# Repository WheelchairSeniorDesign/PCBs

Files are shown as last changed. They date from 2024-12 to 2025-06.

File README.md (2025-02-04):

# PCB Design in Git

- We will be using git to store KiCad files as well so that we can have a running record of them.
- Put all the PCBs in a subfolder in the PCB repo.
- Make a branch for your board, and only work on that board on the corresponding branch.
- Don’t delete your branch once you merge it; keep making changes on that branch.
- Only one person should work on a board at a time, and all changes should be committed before the next person works on it.

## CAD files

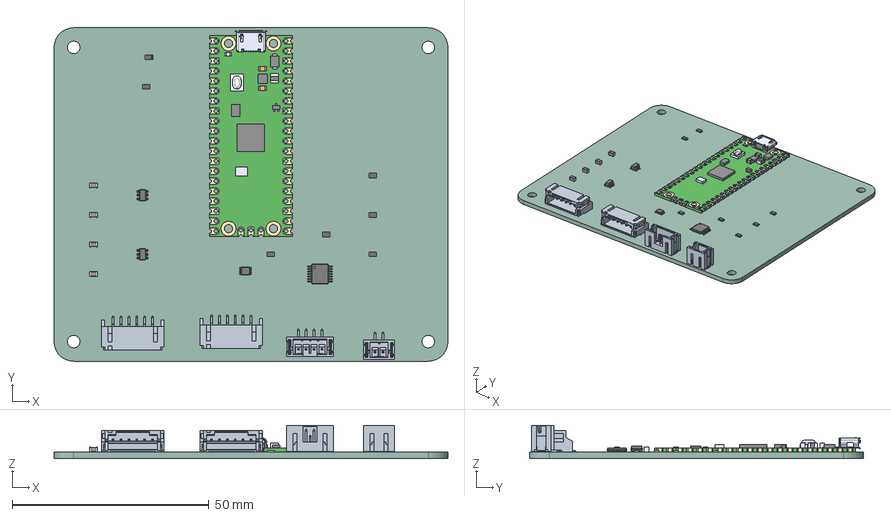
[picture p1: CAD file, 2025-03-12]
MotorSignalConversion/MotorSignalConversion.step
100.0 x 84.7 x 8.40 mm
R_0805_2012Metric x 7
SxBwhite6 x 2
C_0805_2012Metric x 4
B2B-PH-SM4-TB
VSSOP_8_23x2mm_P05mm
SOT_23_6 x 2
TSSOP_14_44x5mm_P065mm
SC0915
B4B-PH-SM4-TB
MotorSignalConversion_PCB

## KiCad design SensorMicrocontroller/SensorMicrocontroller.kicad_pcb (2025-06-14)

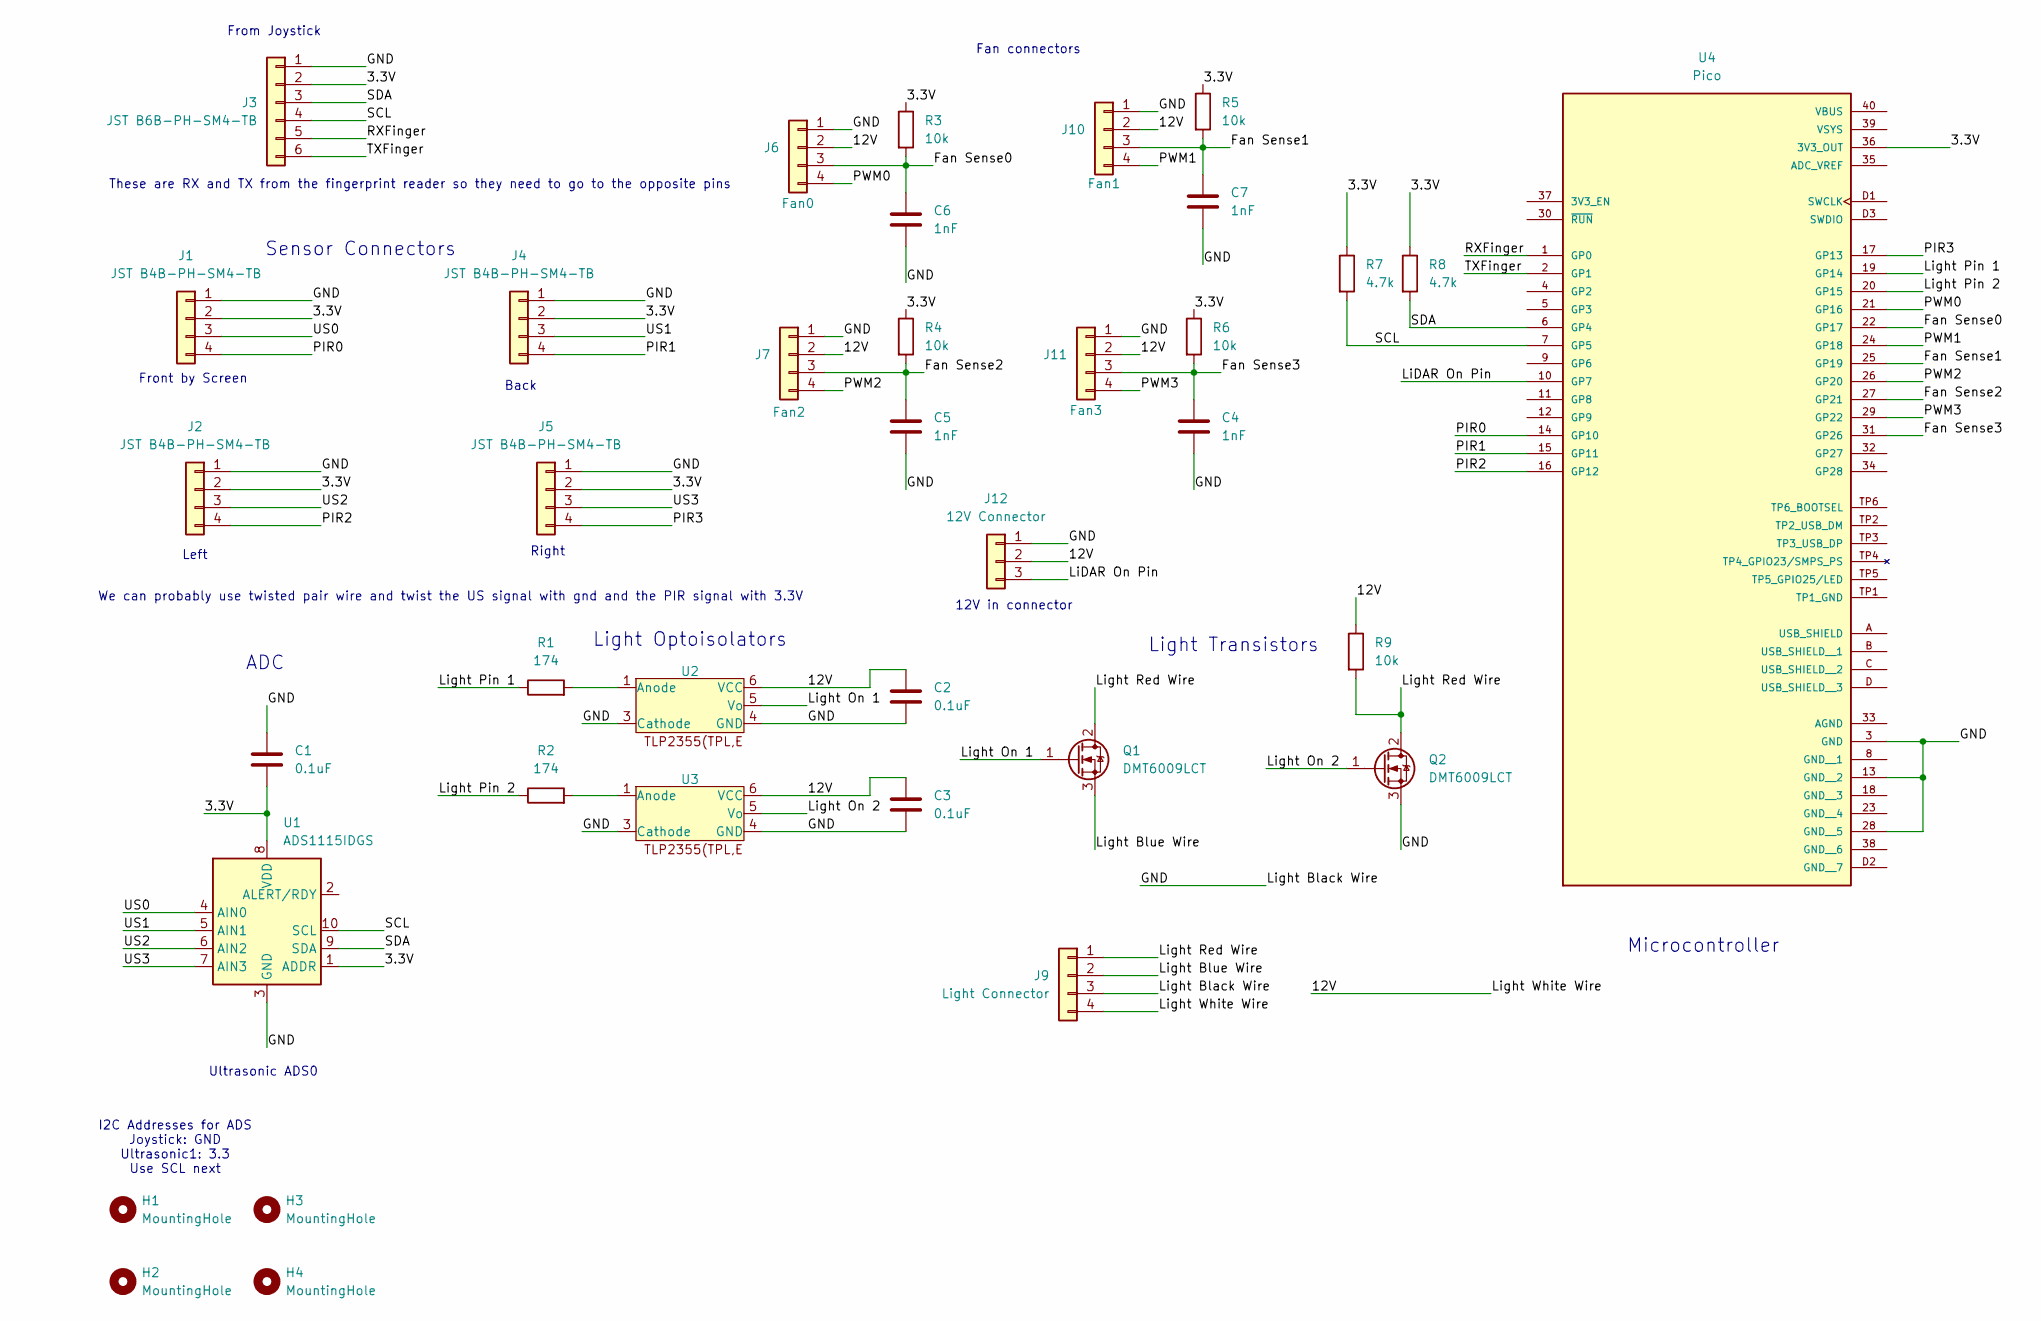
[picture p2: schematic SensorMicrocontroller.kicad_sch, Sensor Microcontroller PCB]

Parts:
C1, C2, C3: 0.1uF; C_0805_2012Metric; Manufacturer Part Number CC0805KRX7R9BB104
C4, C5, C6, C7: 1nF; C_0805_2012Metric; Manufacturer Part Number C0805C102K4RACTU
H1, H2, H3, H4: MountingHole; MountingHole_3.2mm_M3_ISO7380_Pad
J1, J2, J4, J5: JST B4B-PH-SM4-TB; JST_PH_B4B-PH-SM4-TB_1x04-1MP_P2.00mm_Vertical; Manufacturer Part Number B4B-PH-SM4-TB
J3: JST B6B-PH-SM4-TB; JST_PH_B6B-PH-SM4-TB_1x06-1MP_P2.00mm_Vertical; Manufacturer Part Number B6B-PH-SM4-TB
J6, J7, J10, J11: FanPinHeader_1x04_P2.54mm_Vertical; Manufacturer Part Number 0470531000
J9: Light Connector; JST_EH_B4B-EH-A_1x04_P2.50mm_Vertical; Manufacturer Part Number B4B-EH-A
J12: 12V Connector; JST_PH_B3B-PH-SM4-TB_1x03-1MP_P2.00mm_Vertical; Manufacturer Part Number B3B-PH-SM4-TB
Q1, Q2: DMT6009LCT; TO-220-3_Vertical; Manufacturer Part Number DMT6009LCT
R1, R2: 174; R_0805_2012Metric; Manufacturer Part Number RC0805FR-07174RL
R3, R4, R5, R6, R9: 10k; R_0805_2012Metric; Manufacturer Part Number RR1220P-103-D
R7, R8: 4.7k; R_0805_2012Metric; Manufacturer Part Number CRCW08054K70FKEAC
U1: ADS1115IDGS; VSSOP-10_3x3mm_P0.5mm; Manufacturer Part Number ADS1115IDGSR
U2, U3: Optoisolators; SO-5-6_4.55x3.7mm_P1.27mm; Manufacturer Part Number TLP2355(TPL,E
U4: Pico; pico; PARTREV 1.9

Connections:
/3.3V: C1.2, J1.2, J2.2, J3.2, J4.2, J5.2, R3.1, R4.1, R5.1, R6.1, R7.1, R8.1, U1.1 (ADDR), U1.8 (VDD), U4.36 (3V3_OUT)
/12V: C2.1, C3.1, J6.2, J7.2, J9.4, J10.2, J11.2, J12.2, R9.1, U2.6 (VCC), U3.6 (VCC)
/Fan Sense0: C6.1, J6.3, R3.2, U4.22 (GP17)
/Fan Sense1: C7.1, J10.3, R5.2, U4.25 (GP19)
/Fan Sense2: C5.1, J7.3, R4.2, U4.27 (GP21)
/Fan Sense3: C4.1, J11.3, R6.2, U4.31 (GP26)
/GND: C1.1, C2.2, C3.2, C4.2, C5.2, C6.2, C7.2, J1.1, J2.1, J3.1, J4.1, J5.1, J6.1, J7.1, J9.3, J10.1, J11.1, J12.1, Q2.3 (S), U1.3 (GND), U2.3 (Cathode), U2.4 (GND), U3.3 (Cathode), U3.4 (GND), U4.3 (GND), U4.13 (GND__2), U4.28 (GND__5)
/LiDAR On Pin: J12.3, U4.10 (GP7)
/Light Blue Wire: J9.2, Q1.3 (S)
/Light On 1: Q1.1 (G), U2.5 (Vo)
/Light On 2: Q2.1 (G), U3.5 (Vo)
/Light Pin 1: R1.1, U4.19 (GP14)
/Light Pin 2: R2.1, U4.20 (GP15)
/Light Red Wire: J9.1, Q1.2 (D), Q2.2 (D), R9.2
/PIR0: J1.4, U4.14 (GP10)
/PIR1: J4.4, U4.15 (GP11)
/PIR2: J2.4, U4.16 (GP12)
/PIR3: J5.4, U4.17 (GP13)
/PWM0: J6.4, U4.21 (GP16)
/PWM1: J10.4, U4.24 (GP18)
/PWM2: J7.4, U4.26 (GP20)
/PWM3: J11.4, U4.29 (GP22)
/RXFinger: J3.5, U4.1 (GP0)
/SCL: J3.4, R7.2, U1.10 (SCL), U4.7 (GP5)
/SDA: J3.3, R8.2, U1.9 (SDA), U4.6 (GP4)
/TXFinger: J3.6, U4.2 (GP1)
/US0: J1.3, U1.4 (AIN0)
/US1: J4.3, U1.5 (AIN1)
/US2: J2.3, U1.6 (AIN2)
/US3: J5.3, U1.7 (AIN3)
unnamed: R1.2, U2.1 (Anode)
unnamed: R2.2, U3.1 (Anode)

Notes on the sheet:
Microcontroller
Right
ADC
Light Transistors
Back
Sensor Connectors
Left
These are RX and TX from the fingerprint reader so they need to go to the opposite pins
From Joystick
Front by Screen
Fan connectors
Light Optoisolators
Ultrasonic ADS0
I2C Addresses for ADS Joystick: GND Ultrasonic1: 3.3 Use SCL next
12V in connector
We can probably use twisted pair wire and twist the US signal with gnd and the PIR signal with 3.3V

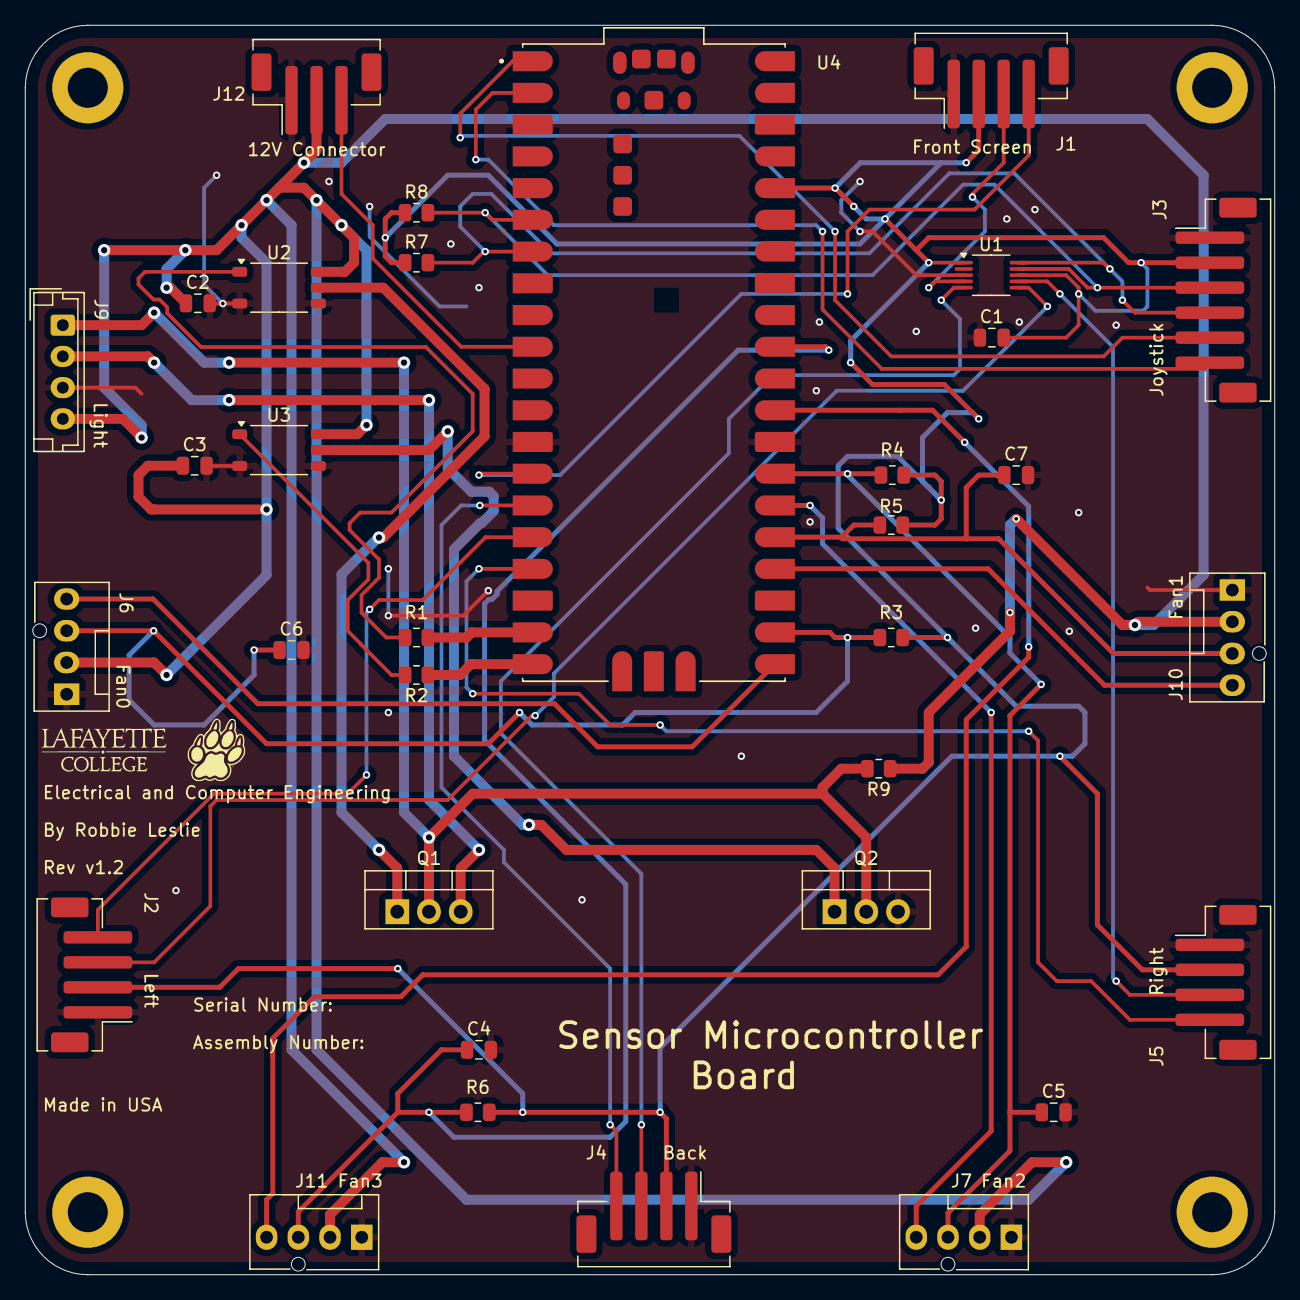
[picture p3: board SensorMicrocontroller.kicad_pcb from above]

Board: 2 copper layers, 100.0 x 100.0 mm, 37 parts (0 on the bottom side), 32 nets.

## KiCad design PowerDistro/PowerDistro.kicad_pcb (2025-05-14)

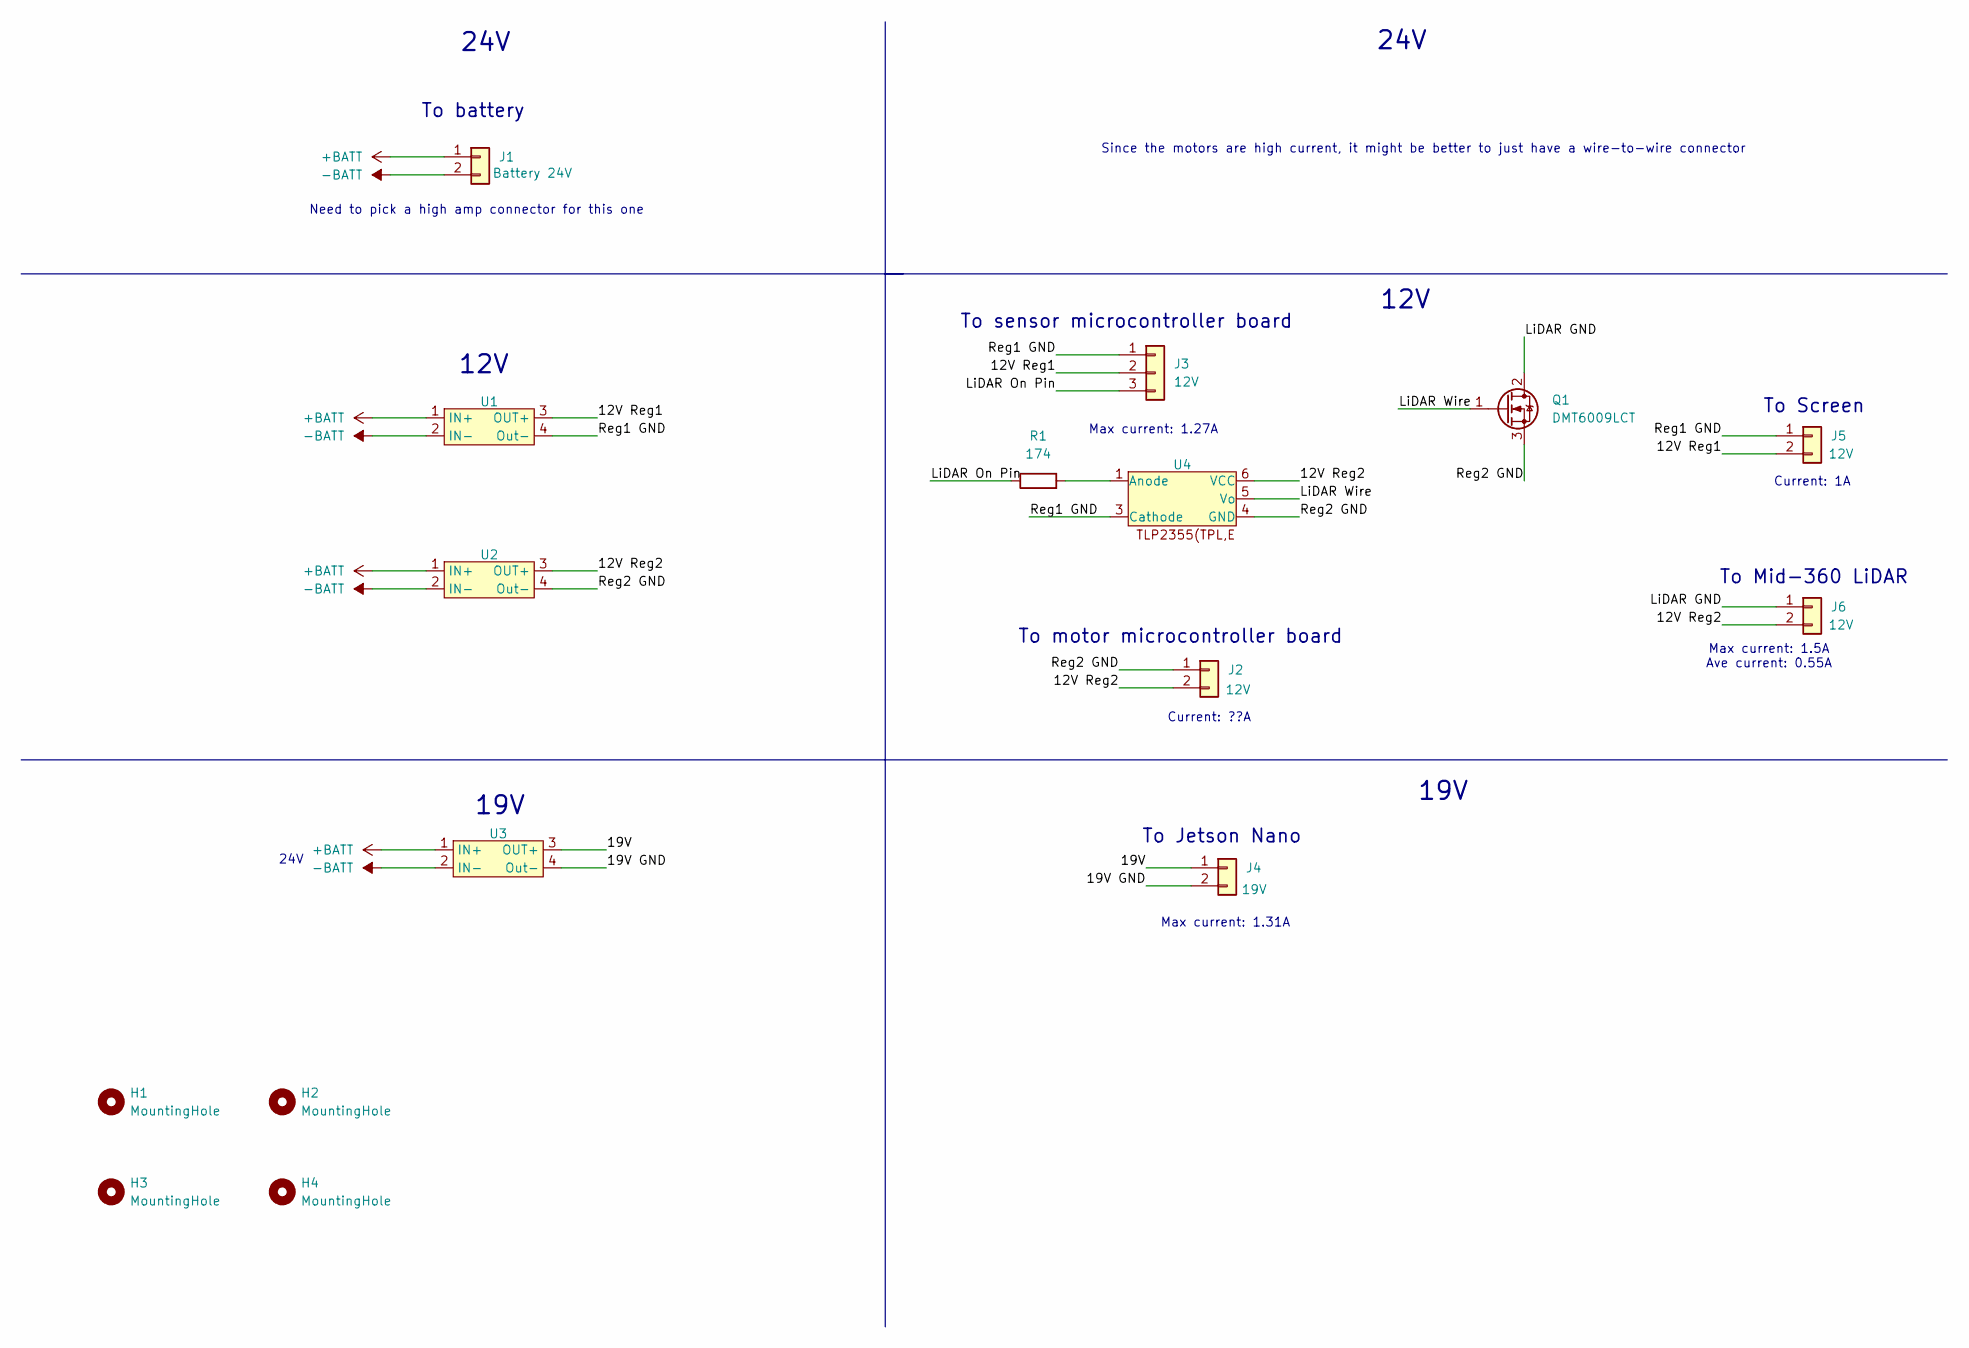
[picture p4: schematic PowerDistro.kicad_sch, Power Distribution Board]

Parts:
H1, H2, H3, H4: MountingHole; MountingHole_3.2mm_M3_ISO7380_Pad
J1: Molex_Mini-Fit_Jr_5566-02A_2x01_P4.20mm_Vertical; Manufacturer Part Number 0039290023
J2: JST_PH_S2B-PH-SM4-TB_1x02-1MP_P2.00mm_Horizontal; Manufacturer Part Number S2B-PH-SM4-TB
J3: 12V; JST_PH_S3B-PH-SM4-TB_1x03-1MP_P2.00mm_Horizontal; Manufacturer Part Number S3B-PH-SM4-TB
J4, J5, J6: JST_XH_S2B-XH-A-1_1x02_P2.50mm_Horizontal; Manufacturer Part Number S2B-XH-A-1
Q1: DMT6009LCT; TO-220-3_Vertical; Manufacturer Part Number DMT6009LCT
R1: 174; R_0805_2012Metric; Manufacturer Part Number RC0805FR-07174RL
U1, U2, U3: LM2596
U4: Optoisolators; SO-5-6_4.55x3.7mm_P1.27mm; Manufacturer Part Number TLP2355(TPL,E

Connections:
+BATT: J1.1, U1.1 (IN+), U2.1 (IN+), U3.1 (IN+)
-BATT: J1.2, U1.2 (IN-), U2.2 (IN-), U3.2 (IN-)
/12V Reg1: J3.2, J5.2, U1.3 (OUT+)
/12V Reg2: J2.2, J6.2, U2.3 (OUT+), U4.6 (VCC)
/19V: J4.1, U3.3 (OUT+)
/19V GND: J4.2, U3.4 (Out-)
/LiDAR GND: J6.1, Q1.2 (D)
/LiDAR On Pin: J3.3, R1.1
/LiDAR Wire: Q1.1 (G), U4.5 (Vo)
/Reg1 GND: J3.1, J5.1, U1.4 (Out-), U4.3 (Cathode)
/Reg2 GND: J2.1, Q1.3 (S), U2.4 (Out-), U4.4 (GND)
unnamed: R1.2, U4.1 (Anode)

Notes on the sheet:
Current: 1A
24V
To Jetson Nano
To battery
19V
12V
Max current: 1.27A
Since the motors are high current, it might be better to just have a wire-to-wire connector
To sensor microcontroller board
To motor microcontroller board
To Mid-360 LiDAR
Need to pick a high amp connector for this one
To Screen
Current: ??A
Max current: 1.5A Ave current: 0.55A
Max current: 1.31A

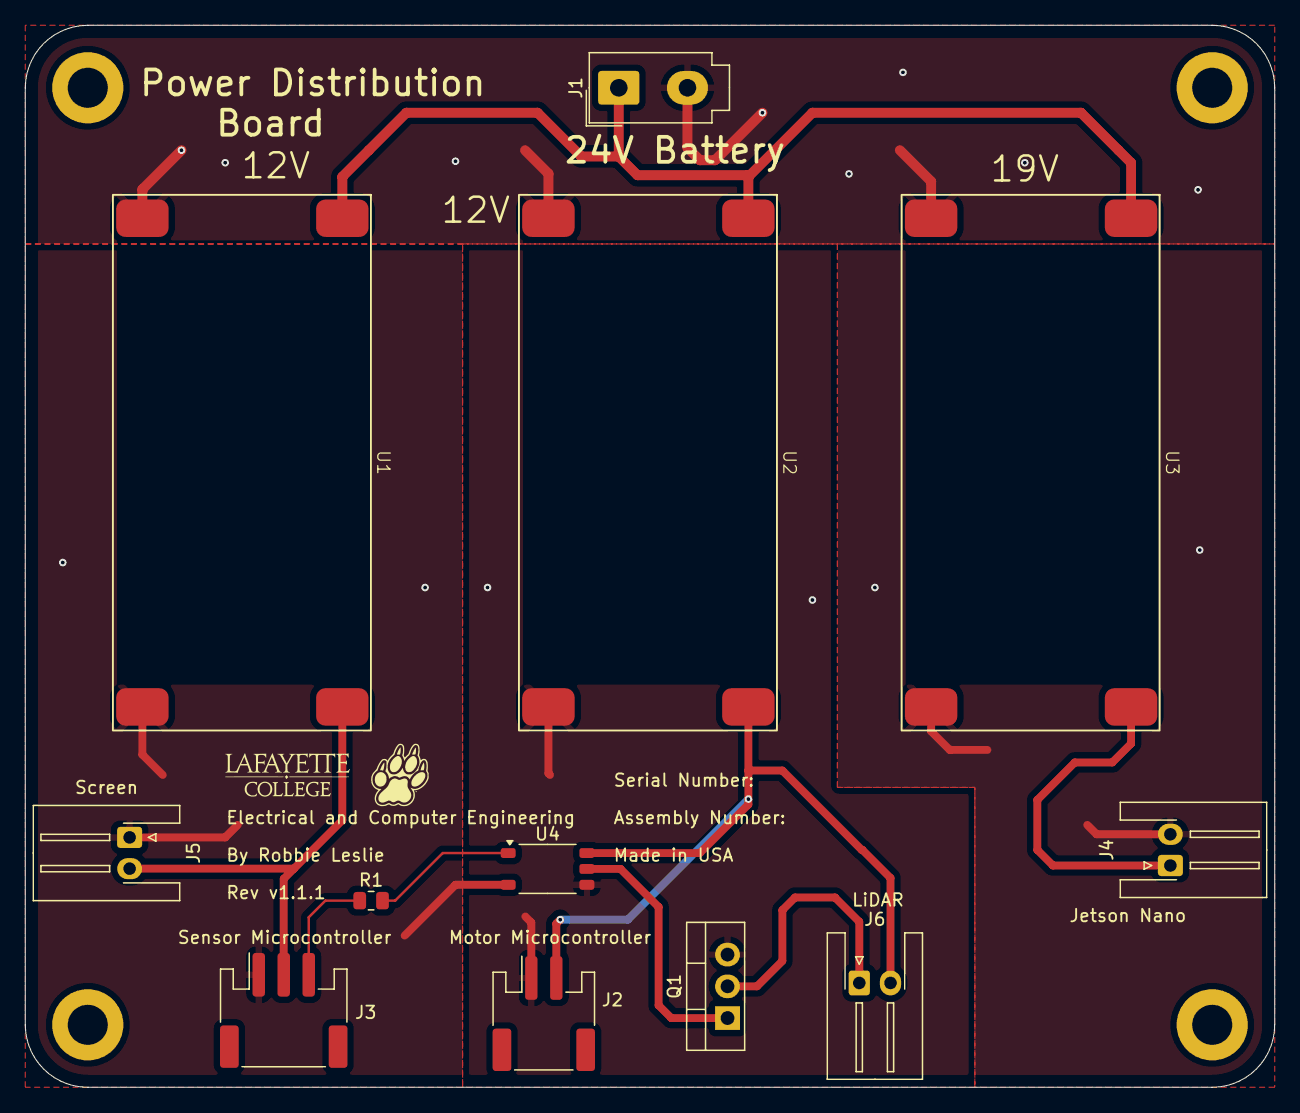
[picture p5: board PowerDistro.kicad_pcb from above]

Board: 2 copper layers, 100.0 x 85.0 mm, 16 parts (0 on the bottom side), 12 nets.

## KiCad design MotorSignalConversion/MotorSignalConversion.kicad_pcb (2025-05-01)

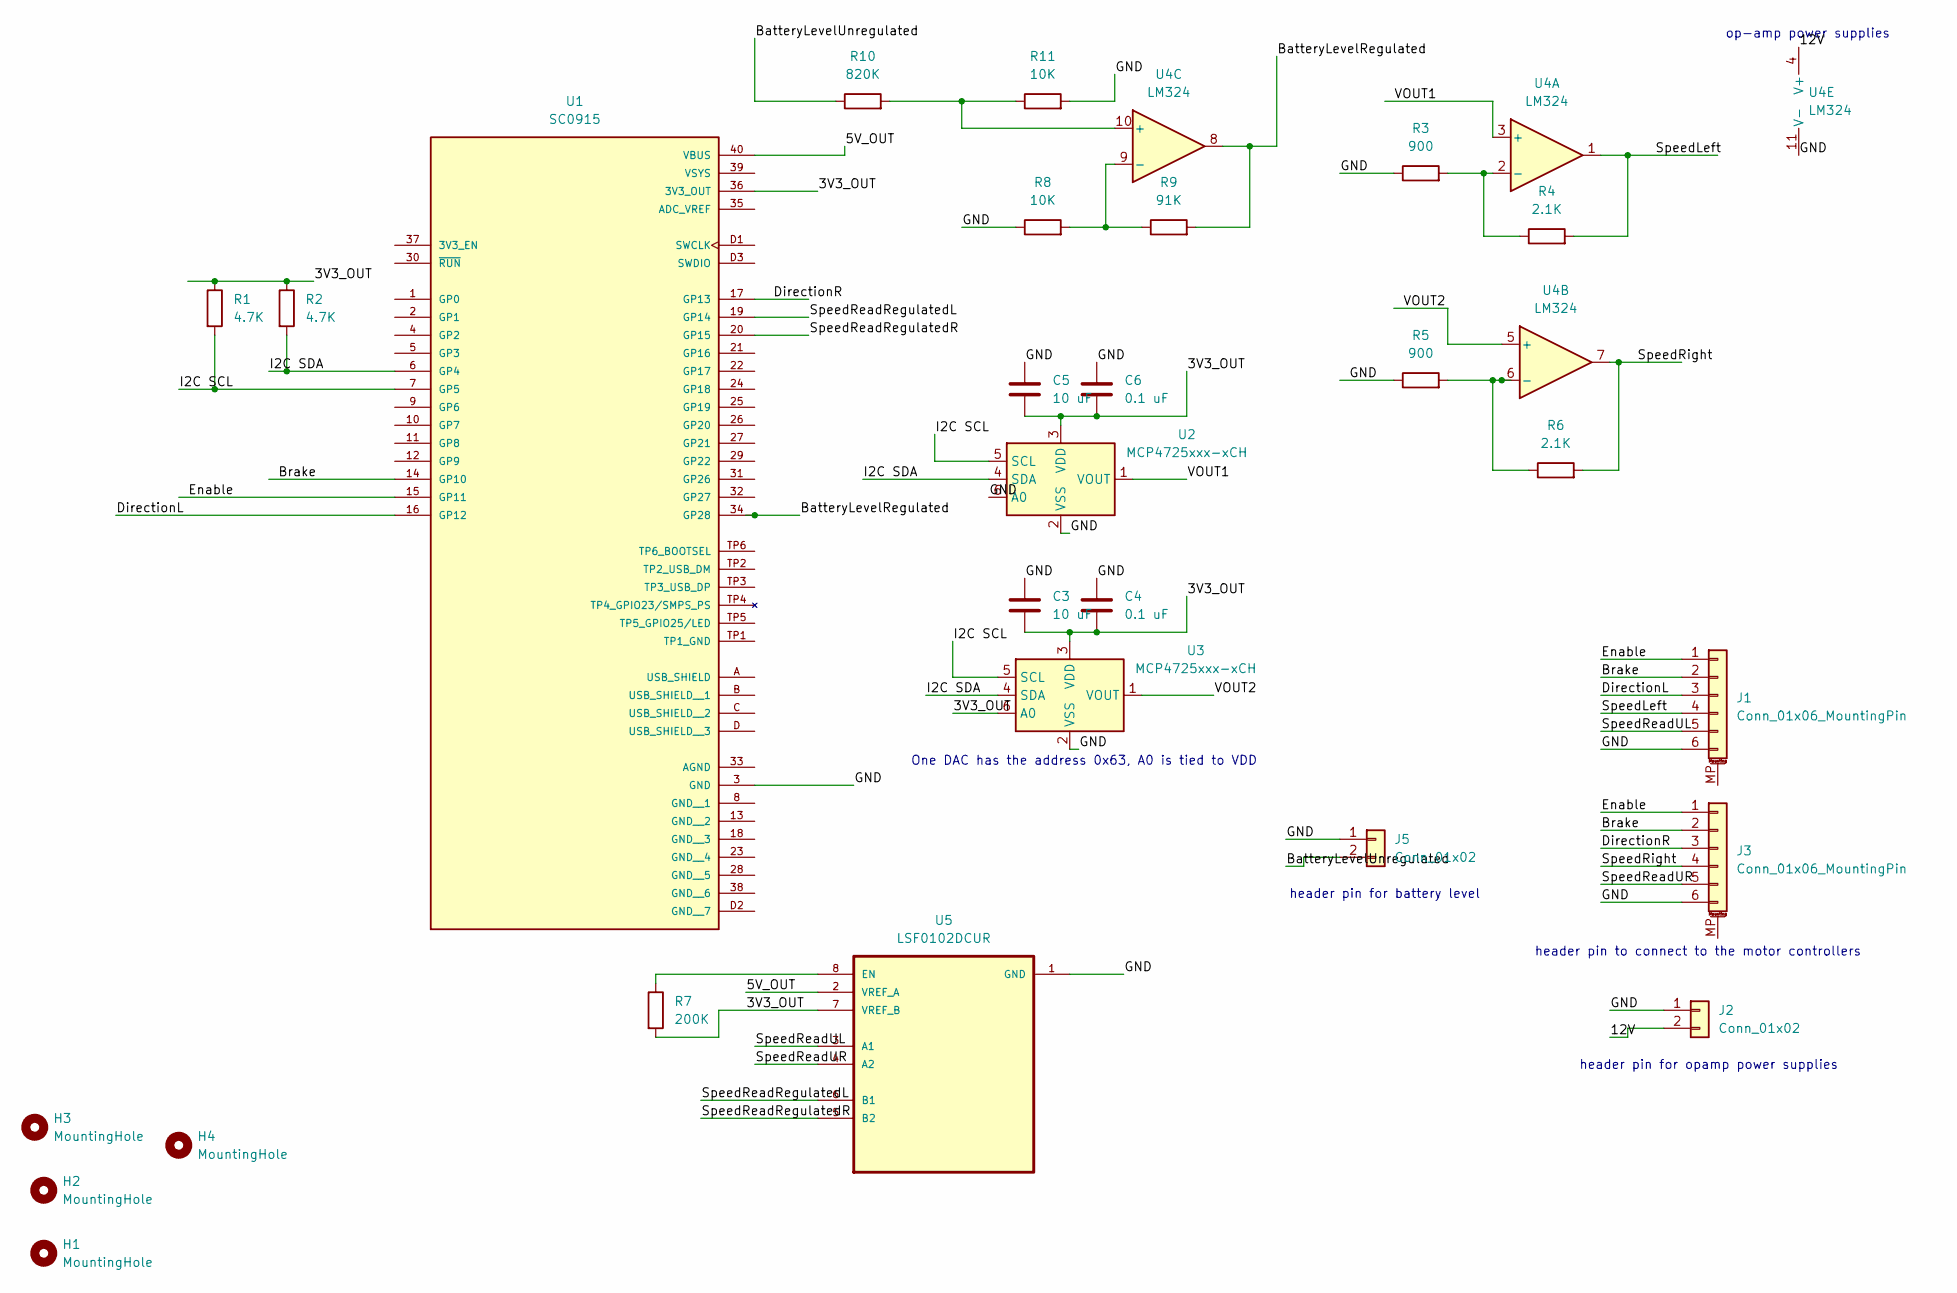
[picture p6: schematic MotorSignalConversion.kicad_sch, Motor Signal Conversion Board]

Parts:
C3, C5: 10 uF; C_0805_2012Metric; Manufacturer Part Number GRM21BR61C106KE15K
C4, C6: 0.1 uF; C_0805_2012Metric; Manufacturer Part Number CC0805KRX7R9BB104
H1, H2, H3, H4: MountingHole; MountingHole_3.2mm_M3_ISO7380_Pad
J1, J3: Conn_01x06_MountingPin; JST_PH_S6B-PH-SM4-TB_1x06-1MP_P2.00mm_Horizontal; Manufacturer Part Number S6B-PH-SM4-TB
J2, J5: Conn_01x02; JST_PH_B2B-PH-SM4-TB_1x02-1MP_P2.00mm_Vertical; Manufacturer Part Number B4B-PH-SM4-TB
R1, R2: 4.7K; R_0805_2012Metric; Manufacturer Part Number CRCW08054K70FKEAC
R3, R5: 900; R_0805_2012Metric; Manufacturer Part Number RC0805FR-07909RL
R4, R6: 2.1K; R_0805_2012Metric; Manufacturer Part Number RC0805FR-072K1L
R7: 200K; R_0805_2012Metric; Manufacturer Part Number ERA-6AEB204V
R8: 10K; R_0805_2012Metric; Manufacturer Part Number RC0805FR-07909RL
R9: 91K; R_0805_2012Metric; Manufacturer Part Number RC0805FR-072K1L
R10: 820K; R_0805_2012Metric; Manufacturer Part Number RC0805FR-07909RL
R11: 10K; R_0805_2012Metric; Manufacturer Part Number RC0805FR-072K1L
U1: SC0915; pico; PARTREV 1.9
U2, U3: MCP4725xxx-xCH; SOT-23-6; Manufacturer Part Number SOT-23-6 MCP4725A1T-E/CH
U4: LM324; TSSOP-14_4.4x5mm_P0.65mm; Manufacturer Part Number LM324PWR
U5: LSF0102DCUR; VSSOP-8_2.3x2mm_P0.5mm; Manufacturer Part Number LSF0102DCUR

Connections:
/3V3_OUT: C3.2, C4.2, C5.2, C6.2, R1.1, R2.1, R7.2, U1.36 (3V3_OUT), U2.3 (VDD), U3.3 (VDD), U3.6 (A0), U5.7 (VREF_B)
/5V_OUT: U1.40 (VBUS), U5.2 (VREF_A)
/12V: J2.2, U4.4 (V+)
/BatteryLevelRegulated: R9.2, U1.34 (GP28), U4.8
/BatteryLevelUnregulated: J5.2, R10.1
/Brake: J1.2, J3.2, U1.14 (GP10)
/DirectionL: J1.3, U1.16 (GP12)
/DirectionR: J3.3, U1.17 (GP13)
/Enable: J1.1, J3.1, U1.15 (GP11)
/GND: C3.1, C4.1, C5.1, C6.1, J1.6, J2.1, J3.6, J5.1, R3.1, R5.1, R8.1, R11.2, U1.3 (GND), U2.2 (VSS), U2.6 (A0), U3.2 (VSS), U4.11 (V-), U5.1 (GND)
/I2C SCL: R1.2, U1.7 (GP5), U2.5 (SCL), U3.5 (SCL)
/I2C SDA: R2.2, U1.6 (GP4), U2.4 (SDA), U3.4 (SDA)
/SpeedLeft: J1.4, R4.2, U4.1
/SpeedReadRegulatedL: U1.19 (GP14), U5.6 (B1)
/SpeedReadRegulatedR: U1.20 (GP15), U5.5 (B2)
/SpeedReadUL: J1.5, U5.3 (A1)
/SpeedReadUR: J3.5, U5.4 (A2)
/SpeedRight: J3.4, R6.2, U4.7
/VOUT1: U2.1 (VOUT), U4.3 (+)
/VOUT2: U3.1 (VOUT), U4.5 (+)
unnamed: R3.2, R4.1, U4.2 (-)
unnamed: R5.2, R6.1, U4.6 (-)
unnamed: R10.2, R11.1, U4.10 (+)
unnamed: R8.2, R9.1, U4.9 (-)
unnamed: R7.1, U5.8 (EN)

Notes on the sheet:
header pin to connect to the motor controllers
header pin for opamp power supplies
header pin for battery level
op-amp power supplies
One DAC has the address 0x63, A0 is tied to VDD

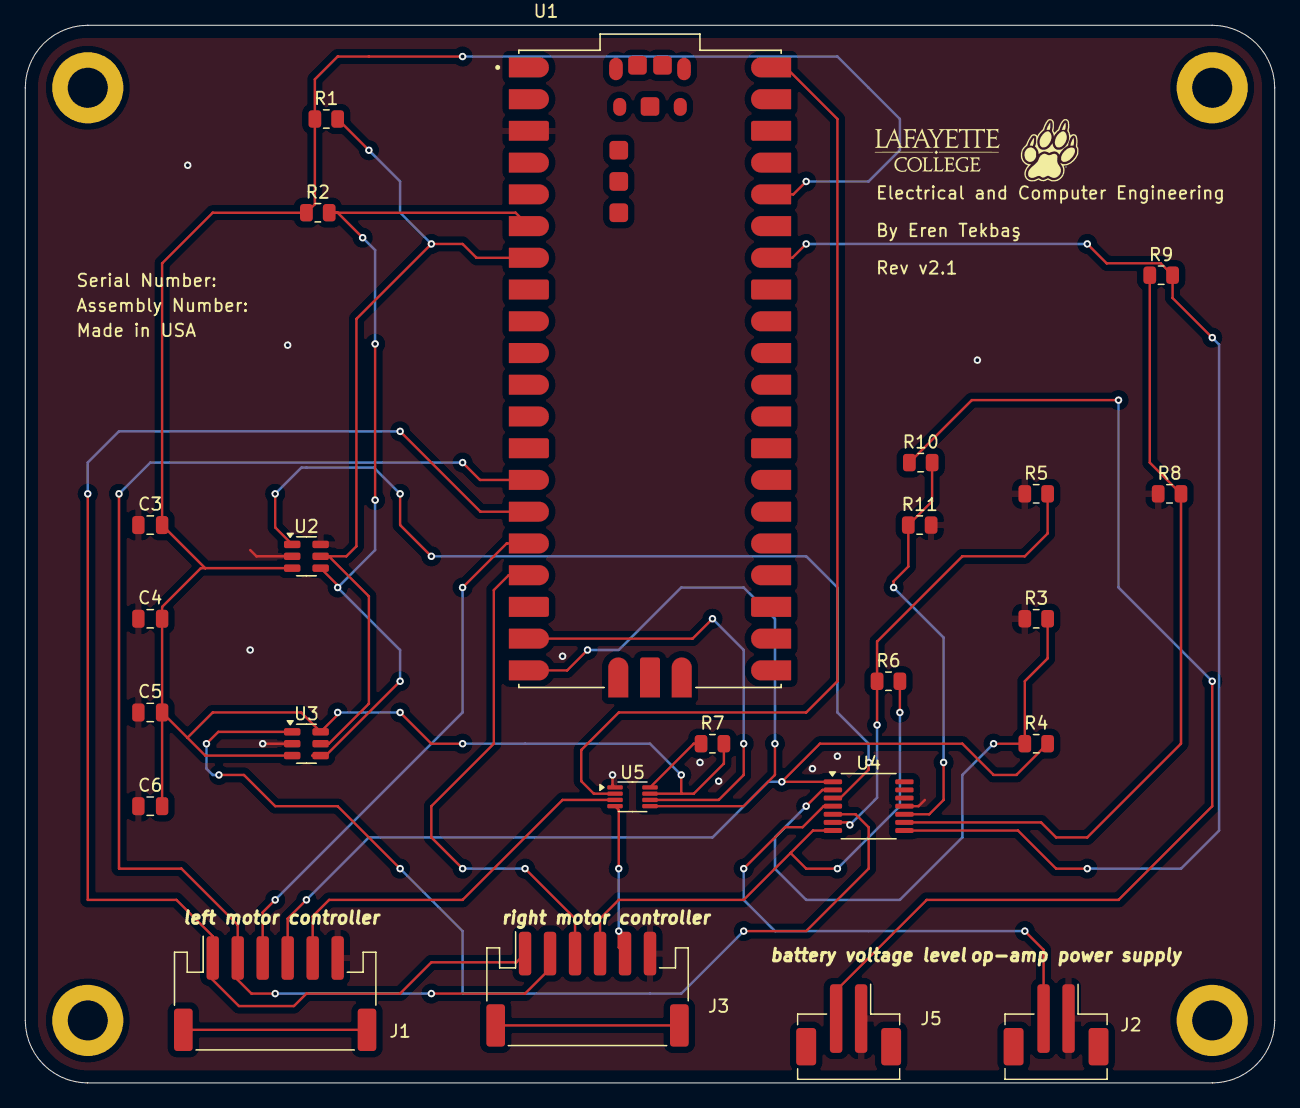
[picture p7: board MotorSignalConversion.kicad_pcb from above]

Board: 2 copper layers, 100.0 x 84.7 mm, 28 parts (0 on the bottom side), 25 nets.

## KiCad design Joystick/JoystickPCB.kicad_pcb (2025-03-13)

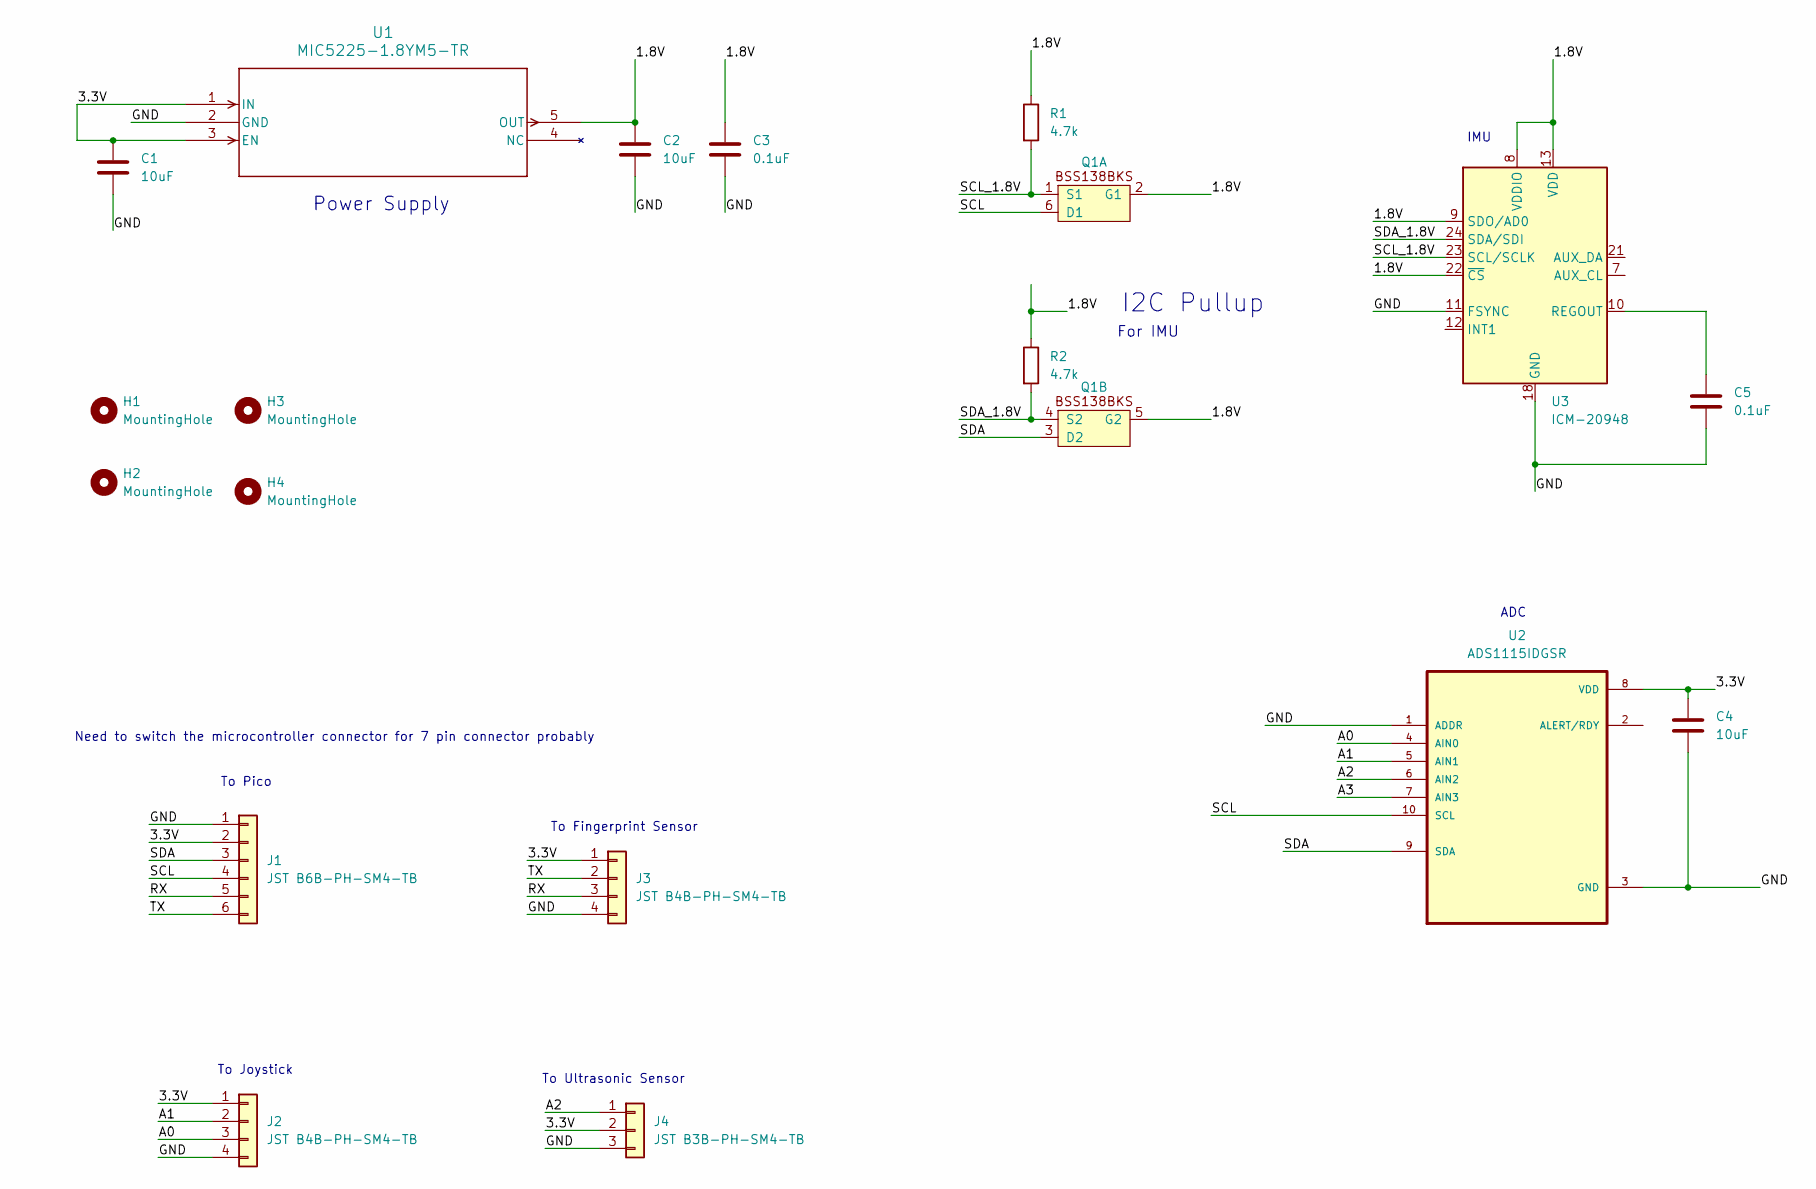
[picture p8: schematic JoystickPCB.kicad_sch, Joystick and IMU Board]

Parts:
C1, C2, C4: 10uF; C_0805_2012Metric; Manufacturer Part Number GRM21BR61C106KE15K
C3, C5: 0.1uF; C_0805_2012Metric; Manufacturer Part Number CC0805KRX7R9BB104
H1, H2, H3, H4: MountingHole; MountingHole_3.2mm_M3_ISO7380_Pad
J1: JST B6B-PH-SM4-TB; JST_PH_S6B-PH-SM4-TB_1x06-1MP_P2.00mm_Horizontal; Manufacturer Part Number S6B-PH-SM4-TB
J2, J3: JST B4B-PH-SM4-TB; JST_PH_B4B-PH-SM4-TB_1x04-1MP_P2.00mm_Vertical; Manufacturer Part Number B4B-PH-SM4-TB
J4: JST B3B-PH-SM4-TB; JST_PH_B3B-PH-SM4-TB_1x03-1MP_P2.00mm_Vertical; Manufacturer Part Number B3B-PH-SM4-TB
Q1: SOT-363_SC-70-6; Manufacturer Part Number BSS138BKS,115
R1, R2: 4.7k; R_0805_2012Metric; Manufacturer Part Number CRCW08054K70FKEAC
U1: MIC5225-1.8YM5-TR; SOT-23-5; Manufacturer Part Number MIC5225-1.8YM5-TR
U2: ADS1115IDGSR; VSSOP-10_3x3mm_P0.5mm; Manufacturer Part Number ADS1115IDGSR
U3: ICM-20948; InvenSense_QFN-24_3x3mm_P0.4mm; Manufacturer Part Number ICM-20948

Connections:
/1.8V: C2.1, C3.1, Q1.2 (G1), Q1.5 (G2), R1.1, R2.1, U1.5 (OUT), U3.8 (VDDIO), U3.9 (SDO/AD0), U3.13 (VDD), U3.22 (~CS)
/3.3V: C1.1, C4.1, J1.2, J2.1, J3.1, J4.2, U1.1 (IN), U1.3 (EN), U2.8 (VDD)
/A0: J2.3, U2.4 (AIN0)
/A1: J2.2, U2.5 (AIN1)
/A2: J4.1, U2.6 (AIN2)
/A3: U2.7 (AIN3)
/GND: C1.2, C2.2, C3.2, C4.2, C5.2, J1.1, J2.4, J3.4, J4.3, U1.2 (GND), U2.1 (ADDR), U2.3 (GND), U3.11 (FSYNC), U3.18 (GND), U3.20 (GND)
/RX: J1.5, J3.3
/SCL: J1.4, Q1.6 (D1), U2.10 (SCL)
/SCL_1.8V: Q1.1 (S1), R1.2, U3.23 (SCL/SCLK)
/SDA: J1.3, Q1.3 (D2), U2.9 (SDA)
/SDA_1.8V: Q1.4 (S2), R2.2, U3.24 (SDA/SDI)
/TX: J1.6, J3.2
unnamed: C5.1, U3.10 (REGOUT)

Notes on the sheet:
For IMU
Need to switch the microcontroller connector for 7 pin connector probably
To Fingerprint Sensor
IMU
To Joystick
I2C Pullup
To Pico
To Ultrasonic Sensor
Power Supply
ADC

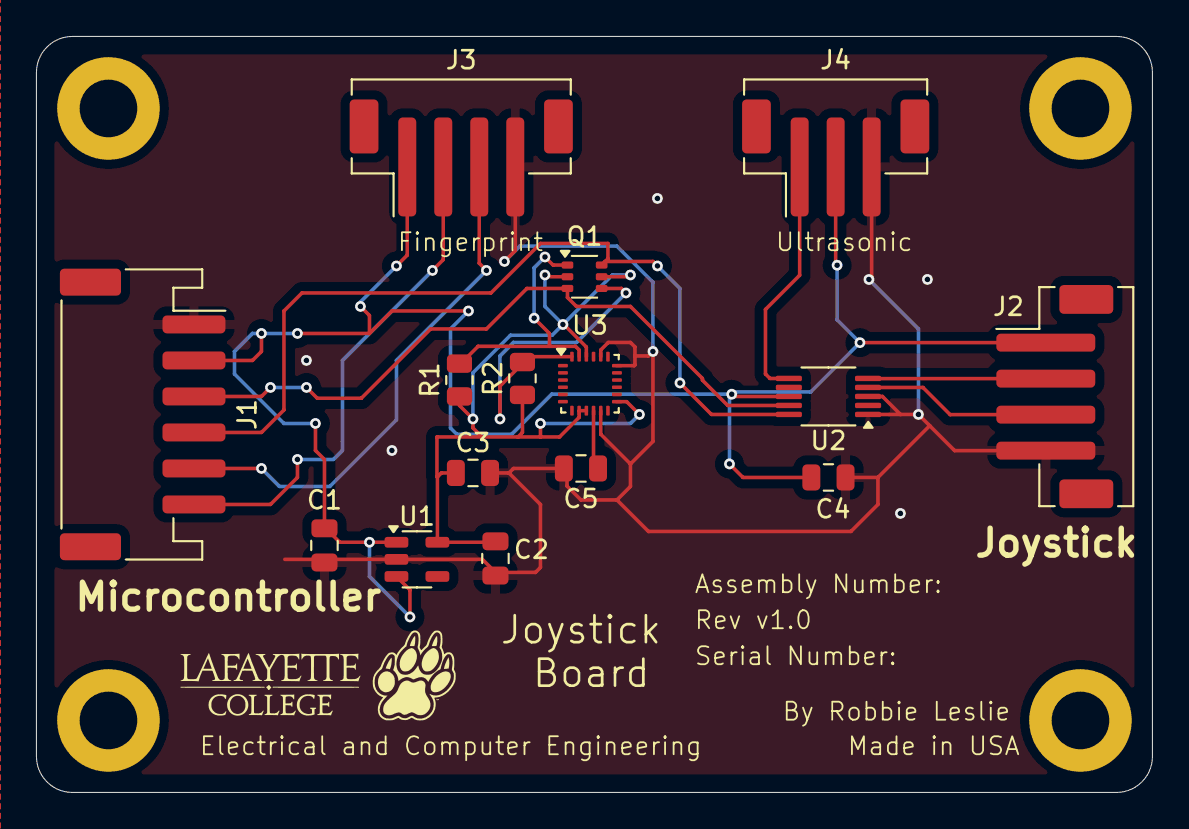
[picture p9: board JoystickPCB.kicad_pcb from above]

Board: 2 copper layers, 62.0 x 42.0 mm, 19 parts (0 on the bottom side), 13 nets.

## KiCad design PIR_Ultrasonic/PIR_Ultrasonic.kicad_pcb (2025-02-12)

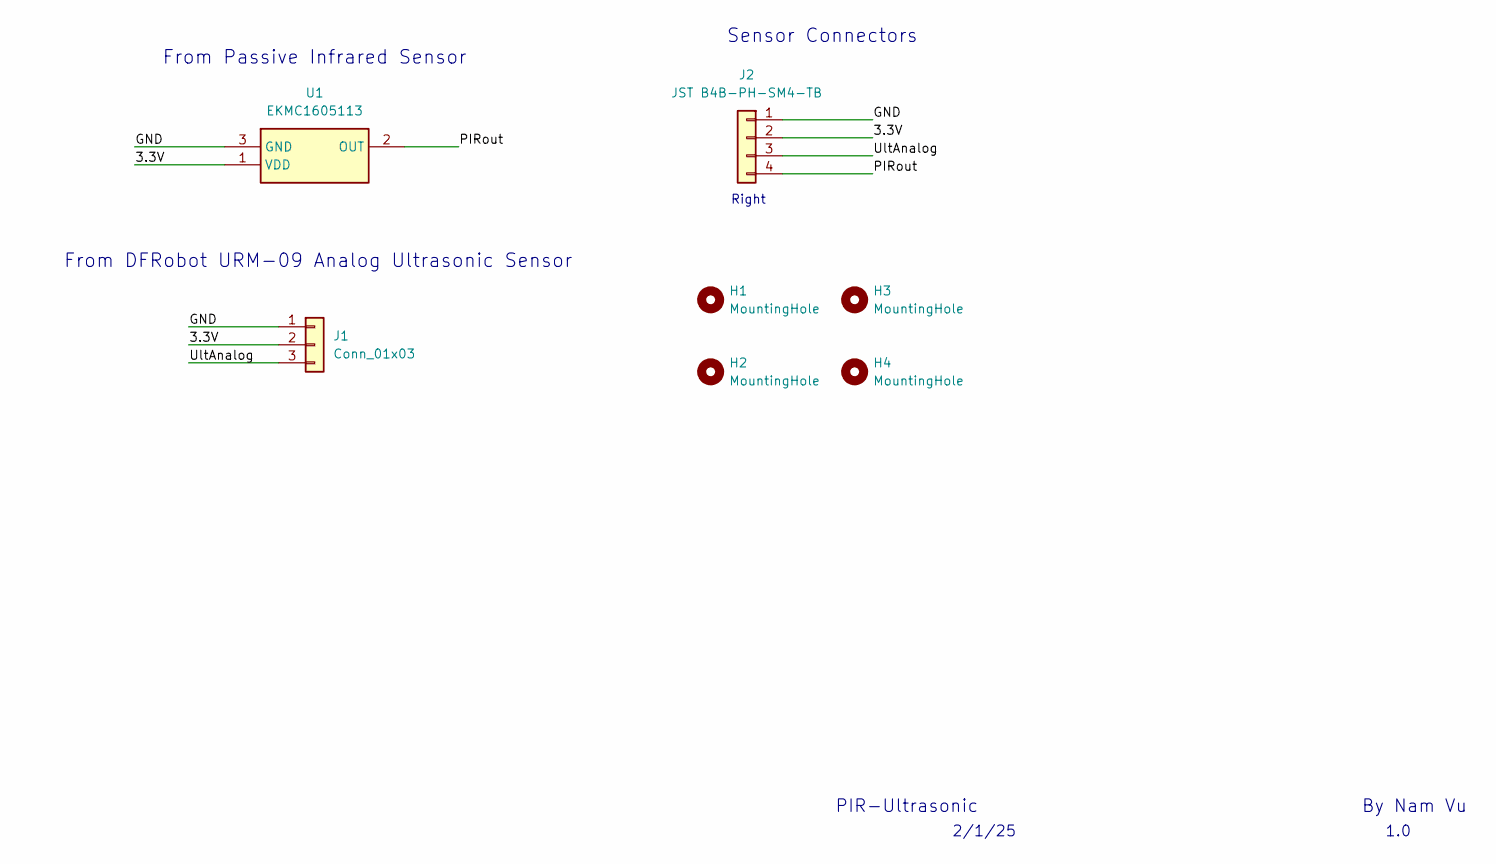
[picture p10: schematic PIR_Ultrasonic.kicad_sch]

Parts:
H1, H2, H3, H4: MountingHole; MountingHole_3.2mm_M3_ISO7380_Pad
J1: Conn_01x03; JST_PH_B3B-PH-SM4-TB_1x03-1MP_P2.00mm_Vertical; Manufacturer Part Number B3B-PH-SM4-TB
J2: JST B4B-PH-SM4-TB; JST_PH_B4B-PH-SM4-TB_1x04-1MP_P2.00mm_Vertical; Manufacturer Part Number B4B-PH-SM4-TB
U1: EKMC1605113; Mouser Part Number 667-EKMC1605113

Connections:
/3.3V: J1.2, J2.2, U1.1 (VDD)
/GND: J1.1, J2.1, U1.3 (GND)
/PIRout: J2.4, U1.2 (OUT)
/UltAnalog: J1.3, J2.3

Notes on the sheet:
From DFRobot URM-09 Analog Ultrasonic Sensor
Right
2/1/25
Sensor Connectors
From Passive Infrared Sensor
1.0
PIR-Ultrasonic
By Nam Vu

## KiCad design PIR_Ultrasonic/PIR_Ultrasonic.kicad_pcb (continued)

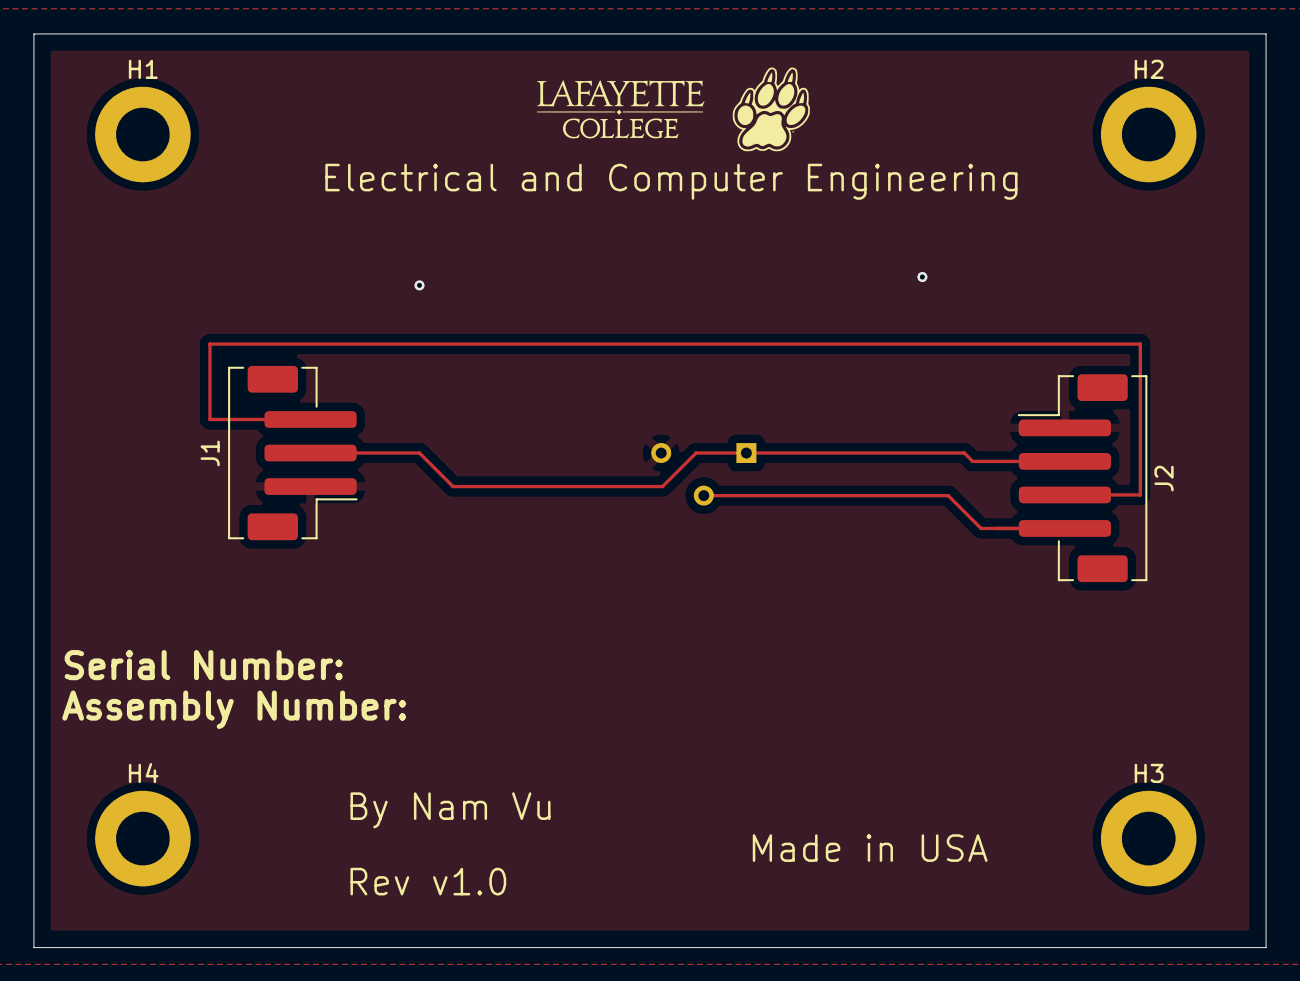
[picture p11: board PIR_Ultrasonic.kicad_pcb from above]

Board: 2 copper layers, 73.5 x 54.5 mm, 7 parts (1 on the bottom side), 4 nets.

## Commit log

2024-10-22 Added KiCAD version of PCB
    [JoystickPCB.kicad_pcb, JoystickPCB.kicad_sch, JoystickTest.PrjPcb, MODULE_SC0915.PcbLib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]
2024-11-07 Schematic should be finished
    [BOM.xlsx, JoystickPCB.kicad_pcb, JoystickPCB.kicad_sch]
2024-11-07 Started work on PCB design
    [JoystickPCB.kicad_pcb, JoystickPCB.kicad_sch]
2024-11-08 Continued work on PCB layout
    [JoystickPCB.kicad_pcb]
2024-11-10 Finished initial PCB design
    [JoystickPCB.kicad_pcb]
2024-11-10 Updated PCB slightly
    [JoystickPCB.kicad_pcb]
2024-11-10 Added some of the required PCB silkscreens
    [JoystickPCB.kicad_pcb]
2024-11-12 Added notes about future revisions
    [JoystickPCB.kicad_sch]
2024-11-13 Rounded corners, updated dimensions, and added comments
    [JoystickPCB.kicad_pcb]
2024-11-14 Moved joystick into sub directory
    [BOM.xlsx, JoystickPCB.kicad_pcb, JoystickPCB.kicad_sch, JoystickTest.PrjPcb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]
2024-11-19 Changed I2C pullups to 4.7k
    [JoystickPCB.kicad_sch]
2024-11-19 Removed extra I2C pullups
    [JoystickPCB.kicad_sch]
2024-11-20 Redesigned PCB with new connectors
    [JoystickPCB.kicad_pcb, JoystickPCB.kicad_sch]
2024-11-21 Updated gitignore and started work on SensorMicrocontroller
    [SensorMicrocontroller.kicad_pcb, SensorMicrocontroller.kicad_sch]
2024-11-21 Removed I2C pullups since they will go on the main board
    [JoystickPCB.kicad_pcb, JoystickPCB.kicad_sch]
2024-11-21 Started work on ultrasonic ADC
    [SensorMicrocontroller.kicad_sch]
2024-11-21 Worked on power for ADS0
    [SensorMicrocontroller.kicad_sch]
2024-11-21 Added connectors for ultrasonic + PIR boards
    [SensorMicrocontroller.kicad_sch]
2024-11-25 Added PWM fan conncectors
    [SensorMicrocontroller.kicad_sch]
2024-11-25 Switch 10uF cap sizes
    [JoystickPCB.kicad_pcb, JoystickPCB.kicad_sch]
2024-11-25 Updated footprint for fan headers
    [SensorMicrocontroller.kicad_pcb, SensorMicrocontroller.kicad_sch]
2024-12-10 Changed logic level shifter for opto-isolator and started work on fan transistors
    [SensorMicrocontroller.kicad_sch]
2025-01-08 Initial wiring for light
    [SensorMicrocontroller.kicad_sch]
2025-01-09 Swapped light connector for JST EH and selected fuse
    [SensorMicrocontroller.kicad_sch]
2025-01-25 Update SensorMicrocontroller.kicad_sch
    updated connections for the light, joystick and biometric sensor
2025-01-27 Revert "Update SensorMicrocontroller.kicad_sch"
2025-01-27 Added manufacturer part number to parts
    [SensorMicrocontroller.kicad_sch]
2025-01-27 Updated date and revision number
    [SensorMicrocontroller.kicad_sch]
2025-01-28 Updated transistor wiring diagram
    [SensorMicrocontroller.kicad_sch]
2025-01-28 Worked on PCB layout
    [SensorMicrocontroller.kicad_pcb, SensorMicrocontroller.kicad_sch]
2025-01-28 Finished PCB layout and started routing
    [SensorMicrocontroller.kicad_pcb, SensorMicrocontroller.kicad_sch]
2025-01-29 Initial version of PCB
    [SensorMicrocontroller.kicad_pcb, SensorMicrocontroller.kicad_sch]
2025-01-29 Added required silkscreen components
    [JoystickPCB.kicad_pcb]
2025-01-29 Added 3D models for PH connectors
    [SensorMicrocontroller.kicad_pcb]
2025-01-29 Updated 3D model positions
    [SensorMicrocontroller.kicad_pcb]
2025-01-29 Delted Altium verison and added some manufacturer part numbers (still need to do R and C)
    [BOM.xlsx, JoystickPCB.kicad_pcb, JoystickPCB.kicad_sch, JoystickTest.PrjPcb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]
2025-01-29 Changed R and C sizes and added part numbers
    [JoystickPCB.kicad_pcb, JoystickPCB.kicad_sch]
2025-01-29 Updated silkscreen
    [SensorMicrocontroller.kicad_pcb]
2025-01-31 Updated trace width for high current components
    [SensorMicrocontroller.kicad_pcb]
2025-01-31 Fixed trace error
    [SensorMicrocontroller.kicad_pcb]
2025-01-31 Updated GND trace widths for more current
    [SensorMicrocontroller.kicad_pcb]
2025-02-02 Switch mounting holes to M3 ISO 7380
    [JoystickPCB.kicad_pcb, JoystickPCB.kicad_sch]
2025-02-02 Swapped M3 screws to ISO 7380
    [SensorMicrocontroller.kicad_pcb, SensorMicrocontroller.kicad_sch]
2025-02-02 Added fill zone
    [SensorMicrocontroller.kicad_pcb]
2025-02-03 Started re-route
    [SensorMicrocontroller.kicad_pcb]
2025-02-03 Continued re-routing traces
    [SensorMicrocontroller.kicad_pcb]
2025-02-03 Finished re-route
    [SensorMicrocontroller.kicad_pcb]
2025-02-03 Added caps for photocouplers
    [SensorMicrocontroller.kicad_pcb, SensorMicrocontroller.kicad_sch]
2025-02-03 Updated fill
    [SensorMicrocontroller.kicad_pcb]
2025-02-04 Updated routing
    [SensorMicrocontroller.kicad_pcb]
2025-02-04 Updated traces
    [JoystickPCB.kicad_pcb]
2025-02-04 Added README for how to use git for PCBs
2025-02-05 Initial schematic for power distro connectors
    [PowerDistro.kicad_pcb, PowerDistro.kicad_sch]
2025-02-06 Removed fan optoisolators after testing them
    [SensorMicrocontroller.kicad_pcb, SensorMicrocontroller.kicad_sch]
2025-02-06 Added a second 12V converter
    [PowerDistro.kicad_sch]
2025-02-07 Added pull up for light transistor after testing
    [SensorMicrocontroller.kicad_pcb, SensorMicrocontroller.kicad_sch]
2025-02-08 Finished picking connectors and started working on layout
    [PowerDistro.kicad_pcb, PowerDistro.kicad_sch]
2025-02-08 Nam draft PIR-Ultrasonic PCB design
    [PIR_Ultrasonic.kicad_pcb, PIR_Ultrasonic.kicad_sch]
2025-02-09 Finished initial layout
    [PowerDistro.kicad_pcb, PowerDistro.kicad_sch]
2025-02-09 Added comments
    [PIR_Ultrasonic.kicad_pcb]
2025-02-09 Added schematic changes
    [PIR_Ultrasonic.kicad_sch]
2025-02-09 Fixed mounting holes positions and general board cleanup
    [JoystickPCB.kicad_pcb, JoystickPCB.kicad_sch]
2025-02-09 Fixed ADS1115 footprint
    [SensorMicrocontroller.kicad_pcb, SensorMicrocontroller.kicad_sch]
2025-02-10 Robbie's comments resolved
    [PIR_Ultrasonic.kicad_pcb]
2025-02-11 Added cap for fan tach
    [SensorMicrocontroller.kicad_pcb, SensorMicrocontroller.kicad_sch]
2025-02-12 Fixed power error on ADC
    [SensorMicrocontroller.kicad_pcb, SensorMicrocontroller.kicad_sch]
2025-02-12 Swapped microcontroller connector for horizontal one
    [JoystickPCB.kicad_pcb, JoystickPCB.kicad_sch]
2025-02-12 Feb 12 changes from Prof Wey's comments
    [PIR_Ultrasonic.kicad_pcb, PIR_Ultrasonic.kicad_sch]
2025-02-13 PCB work in progress before wiring
    [MotorSignalConversion.kicad_pcb, MotorSignalConversion.kicad_sch]
2025-02-14 pcb revision 1 done
    [MotorSignalConversion.kicad_pcb, MotorSignalConversion.kicad_sch]
2025-02-14 added the manufacturer numbers, ready to export a 3d models
    [MotorSignalConversion.kicad_pcb, MotorSignalConversion.kicad_sch]
2025-02-14 Added board part number
    [JoystickPCB.kicad_pcb]
2025-03-03 Added transistor to turn on LiDAR
    [PowerDistro.kicad_sch]
2025-03-03 Updated PCB Layout
    [PowerDistro.kicad_pcb, PowerDistro.kicad_sch]
2025-03-03 Added part number for header
    [PowerDistro.kicad_sch]
2025-03-03 Added 3D model for new header
    [PowerDistro.kicad_pcb]
2025-03-05 Updated powerdistro
    [PowerDistro.kicad_pcb]
2025-03-06 Updated ultrasonic header connection to match with sensor pinout
    [JoystickPCB.kicad_pcb, JoystickPCB.kicad_sch]
2025-03-07 Fixed grounding problem in middle board
    [PowerDistro.kicad_pcb]
2025-03-07 Added LiDAR power controller
    [SensorMicrocontroller.kicad_pcb, SensorMicrocontroller.kicad_sch]
2025-03-07 Swapped to XH-A-1 connector and added mounting hole stencil cutouts
    [PowerDistro.kicad_pcb, PowerDistro.kicad_sch]
2025-03-07 Updated board version number
    [SensorMicrocontroller.kicad_pcb, SensorMicrocontroller.kicad_sch]
2025-03-07 Updated rivision silkscreen
    [PowerDistro.kicad_pcb]
2025-03-10 added the schematic for the battery circuit
    [MotorSignalConversion.kicad_pcb, MotorSignalConversion.kicad_sch, MotorSignalConversion.step]
2025-03-12 revised PCB design, added text for connectors
    [MotorSignalConversion.kicad_pcb]
2025-03-12 Updated SensorMicrocontroller design
    [SensorMicrocontroller.kicad_pcb, SensorMicrocontroller.kicad_sch]
2025-03-13 revised based on feedback
    [MotorSignalConversion.kicad_pcb, MotorSignalConversion.kicad_sch]
2025-03-13 fixed the issue with resistors for i2c
    [MotorSignalConversion.kicad_pcb]
2025-03-14 fixed opamp gnd issue
    [MotorSignalConversion.kicad_pcb]
2025-03-14 added vials to fix ground
    [MotorSignalConversion.kicad_pcb]
2025-03-14 Fixed unconnected ground
    [MotorSignalConversion.kicad_pcb]
2025-05-14 Updated silkscreen on power distro board
    [PowerDistro.kicad_pcb]
2025-06-14 Fixed 12V silkscreen on sensor board
    [SensorMicrocontroller.kicad_pcb]
